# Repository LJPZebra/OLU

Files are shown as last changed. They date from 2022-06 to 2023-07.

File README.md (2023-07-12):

# A Versatile and Open Source One- and Two-Photon Light-Sheet Microscope Design

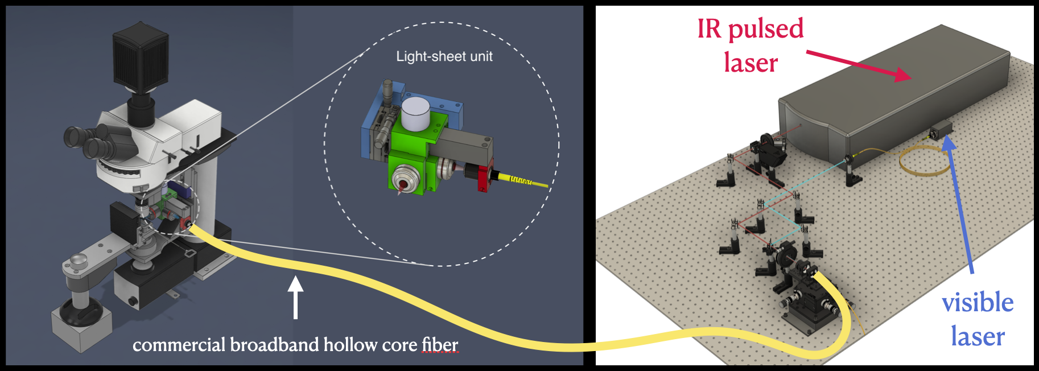
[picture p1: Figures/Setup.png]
Setup


Two-photon light sheet microscopy offers great potential for a range of biological applications, but its practical implementation is impeded by the high cost of laser sources, the complexity of construction, and the challenges associated with adapting to existing microscope setups. Here, we release an open-source design that addresses these limitations by providing detailed building instructions for the transformation of a brightfield microscope into a versatile one- and two-photon light sheet system.
Our design incorporates a specially designed broadband hollow core fiber, enabling the simultaneous utilization of an expansive pulsed laser source from another setup alongside a visible laser. This integration allows for uncompromised image resolution and speed. Furthermore, the design reduces the complexity of construction, alignment, and overall cost, thereby significantly enhancing the accessibility of this technology.

## BUILDING INSTRUCTIONS:

Here we provide a comprehensive online tutorial that features step-by-step building instructions along with 3D animations, illustrations of the construction process, detailed information on the underlying physical principles, and rationale for components selection. In conjunction with the availability of commercially accessible and connectorized broadband optical fiber, our aim is to promote greater accessibility and affordability in the field of multiphoton light-sheet microscopy. To access this online resource, please follow the links provided below: 

1. [Build first a multicolor one-photon version of the microscope](1P_Multicolor_System.md) with fiber delivery of lasers in the visible spectrum with a standard single-mode optical fiber technology.

2. [Upgrade the one-photon unit into a two-photon system](2P-Upgrade.md) by exploiting advanced hollow core fiber technology.

## Citation:

If you use the hardware designs, please cite us:

[A Versatile and Open Source One- and Two-Photon Light-Sheet Microscope Design](https://biorxiv.org/cgi/content/short/2023.07.10.548107v1)

Thomas Panier\*, Geoffrey Migault\*, Antoine Hubert, Hugo Trentesaux, Benoît Beaudou, Georges Debrégeas, Volker Bormuth

https://biorxiv.org/cgi/content/short/2023.07.10.548107v1

https://github.com/LJPZebra/OLU/assets/38736127/4a50b8ec-c064-456c-bfb1-02f57ff8efe5

<!--- 
## Explorable 3D model of the full system

[<img width="600" alt="FullSystem_3D-Model" src="Figures/FullSystem_3D-Model.png">](https://a360.co/41PexBK)

[<img width="600" alt="2P_laser_injection_3D-Model" src="Figures/2P_laser_injection_3D-Model.png">](https://a360.co/3JVrDGn)

Click the images to open the model browser.

## 3D Animation of the functionality of the system

https://github.com/vbormuth/OLU/assets/38736127/af95fe67-40c8-4dab-be80-82982df7b801

## Slow scan mode

https://user-images.githubusercontent.com/113037893/207926697-6573f5d4-6586-4915-aaef-1366d4b2105a.mp4

## Fast scan mode

https://user-images.githubusercontent.com/113037893/207927665-f9e60bf5-719b-4414-81f9-21bd3844fda7.mp4

## High-resolution zebrafish brain scans (elav3:H2B-GCaMP6)

* Left: one-photon mode excited @ 488nm
* Right:  two-photon mode excited @ 915nm

https://user-images.githubusercontent.com/38736127/178161973-748767bf-004d-487c-9377-4582a705d8d7.mp4

## Spontaneous brain activity recorded in a two-photon mode

https://user-images.githubusercontent.com/38736127/174909302-b3901000-2807-471f-93b6-27f24e98cbe1.mp4

## CAD models

[CAD models](CAD_models)

--->

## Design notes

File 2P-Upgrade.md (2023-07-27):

# Two-photon upgrade

This comprehensive guide provides detailed instructions for upgrading the system to the two-photon configuration. Assuming that you have already built the one-photon version of the system, the upgrade primarily involves two main steps. First, you need to fiber couple a two-photon femtosecond pulsed laser into a negative hollow-core optical fiber. Additionally, the fiber's numerical aperture at the output side should be increased for compatibility with the light-sheet unit. Secondly, if not already implemented, the objectives used in the light-sheet unit must be replaced with objectives optimized for near-infrared transmission. Finally, a filter must be installed in the detection path to block the infrared laser. These modifications will enable efficient two-photon imaging with the system.

# Table of Content

- [Part List](#part-liste)
  * [Custom Parts to Send for Milling](#custom-parts-to-send-for-milling)
- [Building Instructions](#building-instructions)
  * [Multiphoton Light-Sheet Unit](#multiphoton-light-sheet-unit)
  * [A Comprehensive Guide for Achieving Efficient Fiber Coupling of the Femtosecond Two-Photon Laser](#a-comprehensive-guide-for-achieving-efficient-fiber-coupling-of-the-femtosecond-two-photon-laser)
    + [Introducing Our Developed Negative Curvature Hollow Core Crystal Fiber](#introducing-our-developed-negative-curvature-hollow-core-crystal-fiber)
    + [The Optical Path for Laser-to-Fiber Coupling](#the-optical-path-for-laser-to-fiber-coupling)
    + [Tips and Techniques for Laser Coupling into the Broadband Hollowcore Crystal Fiber](#tips-and-techniques-for-laser-coupling-into-the-broadband-hollowcore-crystal-fiber)
    + [Mastering the Handling of Hollow Core Fibers: Tips and Techniques](#mastering-the-handling-of-hollow-core-fibers--tips-and-techniques)
    + [Selecting the Optimal Coupling Lens: Criteria and Considerations](#selecting-the-optimal-coupling-lens--criteria-and-considerations)
    + [Let's Get Started: Building the System](#let-s-get-started--building-the-system)
      - [Coupling the IR Laser into the Broadband Fiber](#coupling-the-ir-laser-into-the-broadband-fiber)
      - [Coupling the Visible Laser into the Broadband Fiber](#coupling-the-visible-laser-into-the-broadband-fiber)
  * [Increasing the Fiber Numerical Aperture for Compatibility with the Light-Sheet Unit](#increasing-the-fiber-numerical-aperture-for-compatibility-with-the-light-sheet-unit)
  * [Modifying the Fluorescence Detection Path to Block Infrared Illumination](#modifying-the-fluorescence-detection-path-to-block-infrared-illumination)
  * [Alignement of the setup](#alignement-of-the-setup)
  * [Example of High-Resolution Zebrafish Brain Recordings in One- and Two-Photon Mode (elav3:H2B-GCaMP6)](#example-of-high-resolution-zebrafish-brain-recordings-in-one--and-two-photon-mode--elav3-h2b-gcamp6-)

<small><i><a href='http://ecotrust-canada.github.io/markdown-toc/'>Table of contents generated with markdown-toc</a></i></small>

# Part List

[List of parts](Partlist.md)

## Custom Parts to Send for Milling
    
These parts are  milled from an aluminum block. If you do not have a mechanical workshop in-house then you can send the *.step files that we provide below to an [online milling service](https://xometry.eu/fr/usinage-cnc-fraisage-cnc/). For parts with threaded holes, join the mechanical drawings to the .step file.
* Custom part for compatibility with a MaiTai laser: [View the 3D model](CAD_models/NanoMax_Pedestal.stl) or [download the CAD model as a step file](CAD_models/NanoMax_Pedestal.step) and the [Mechanical drawing](CAD_models/NanoMax_Pedestal.pdf).

# Building Instructions

## Multiphoton Light-Sheet Unit

The multiphoton light-sheet unit is basically identical in its design to the one-photon multicolor design. To build the two-photon system follow [the building instruction of the 1P-Multicolor system](1P_Multicolor_System.md) but take into account the following modification: 

For both the collimation and illumination objectives (step (9) of the building instruction of the Light-sheet Unit), use the [Olympus LMPLN5xIR/0.1](https://www.olympus-lifescience.com/modules/pdfgen/pdfmaker/en_pdf-export_objectives.7efd53eb1e8b4d509bc1bbe2184a7e28/LMPLN5XIR.pdf?rev=1615725199) objective optimized for near-infrared transmission. Although it is not optimized for visible wavelength, one can use this objective for one-photon imaging as well. To screw it into the light-sheet cube use a [thread adaptor](https://punchout.webdev02.thorlabs.com/thorproduct.cfm?partnumber=RMSA3).

## A Comprehensive Guide for Achieving Efficient Fiber Coupling of the Femtosecond Two-Photon Laser

<!--- ### Historical Background

[IS THIS SECTION useful ?]

Efficient, dispersion-free, and broadband fiber coupling of a two-photon laser source is a long-standing challenge in the field of two-photon microscopy ([Helmchen et al., 2011](http://cshprotocols.cshlp.org/content/2013/10/pdb.top078147.long)) and of fiber optics design ([Wang et al., 2013](https://www.cambridge.org/core/journals/high-power-laser-science-and-engineering/article/hollowcore-photonic-crystal-fibre-for-high-power-laser-beam-delivery/8D2851845D043DA937A93F431D9F9D9C)). The difficulty arises from the fact that standard single-mode optical glass fibers are associated with strong linear and non-linear pulse dispersion, which reduces the two-photon efficiency. Pre-compensation methods are only efficient at low laser powers and are therefore impractical in the context of fast volumetric two-photon imaging, which requires high photonic fluxes. 

The development of single-mode photonic bandgap fibers, in which the light travels through an air-filled hollow core, dramatically reduces dispersion and nonlinear effects and achieves transmission ratios greater than 50% ([Wang et al., 2013](https://www.cambridge.org/core/journals/high-power-laser-science-and-engineering/article/hollowcore-photonic-crystal-fibre-for-high-power-laser-beam-delivery/8D2851845D043DA937A93F431D9F9D9C), [Cregan et al., 1999](https://www.science.org/doi/10.1126/science.285.5433.1537)). These fibers have been successfully used for pulsed laser delivery in the context of multiphoton imaging ([Tai et al., 2004](https://opg.optica.org/abstract.cfm?URI=oe-12-25-6122), [Flusberg et al., 2005](https://opg.optica.org/abstract.cfm?URI=ol-30-17-2272), [Engelbrecht et al., 2008](https://opg.optica.org/abstract.cfm?URI=oe-16-8-5556), [Piyawattanametha et al., 2009](https://opg.optica.org/abstract.cfm?&uri=ol-34-15-2309), [Choi et al., 2014](https://www.nature.com/articles/srep06626)). However, as the light guiding mechanism is based on the creation of an optical bandgap, these fibers only allow single-wavelength transmission and are currently only commercially available for laser wavelengths of 800 nm or 1064 nm (NTK photonics). However, with the rapidly growing collections of genetically encoded actuators and sensors, broadband fiber delivery of the near-infrared spectrum and optimally extended to visible wavelengths, is a prerequisite to taking full advantage of 2P-LSFM in all possible applications while enabling laser source sharing between different setups.

Broadband fiber delivery spanning the visible and the near-infrared spectrum is possible with negative curvature hollow-core photonic crystal fibers (NCF), which do not rely on an optical bandgap to confine the laser light to the fiber's core ([Yu et al., 2016](https://opg.optica.org/abstract.cfm?URI=oe-24-12-12969), [Pryamikov et al., 2011](https://opg.optica.org/abstract.cfm?URI=oe-19-2-1441), [Yu et al., 2012](https://doi.org/10.1364/OE.20.011153)). The simplest cross-sectional geometry of an NCF is based on a ring of touching or non-touching tubes surrounding the core ([Pryamikov et al., 2011](https://opg.optica.org/abstract.cfm?URI=oe-19-2-1441)). Core diameter, tube diameter, inter-tube distance, and tube wall thickness together control the spectral transmission bands, the attenuation level, the quality of higher-order mode suppression, and the sensitivity of the optical properties to bending. Attenuation levels < 0.07 dB/km and bending loss < 0.03 dB/m are reported ([Debord et al., 2017](https://doi.org/10.1364/OPTICA.4.000209)). Due to the minimal lattice structure and the reduced light interaction with the cladding structure, these fibers have very high damage thresholds and can even be used for very high laser energy delivery of up to 100 $\mu\textrm{J}$ peak power when the core is vacuum pumped to reduce nonlinear effects at these high powers ([Li et al., 2019](https://doi.org/10.1016/j.ijleo.2019.163093)). Negative curvature fibers are on the verge of being used in several applications such as laser micromachining and laser surgery. A recent study demonstrated the successful use of a custom HC-NCF with a transmission band of 600 – 830 nm at < 0.3 dB/m attenuation in the design of a handheld two-photon microscopy scanner for human skin autofluorescence ([Sherlock et al., 2016](https://doi.org/10.1002/jbio.201500290)).
--->
### Introducing Our Developed Negative Curvature Hollow Core Crystal Fiber

Together with [GLO Photonics](https://www.glophotonics.fr/), we selected an HC-NCF fiber whose optical characteristics are ideally suited for laser delivery in the context of combined one- and two-photon light-sheet microscopy. 

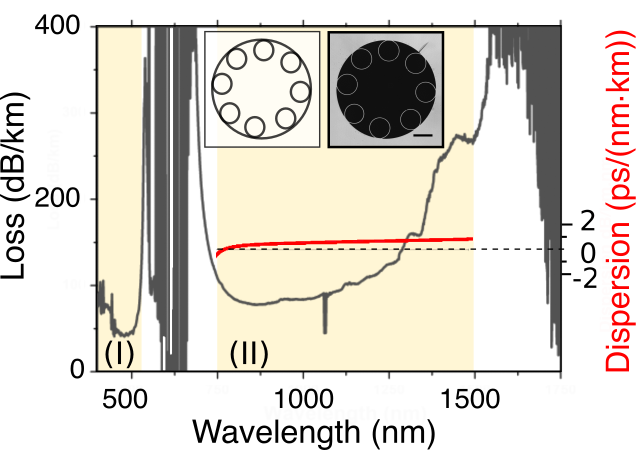
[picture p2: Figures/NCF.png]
NCF
[](Figures/NCF.png)

The outer fiber diameter is 200 ± 2 μm and the fiber coating diameter is 600 ± 30 μm. The fiber has an air-filled 30 μm-in-diameter core surrounded by a ring of eight non-contacting ~10 μm-in-diameter cladding tubes. In this so-called hypocycloid fiber structure, the negative curvature of the core contour is created by the tubes surrounding the core. Tube diameters, inter-tube distance, tube wall thickness, and core size together control the fiber transmission spectrum. They yield two broad transmission bands that are compatible with 1, 2, and 3P imaging, respectively (see figure above): One in the near-infrared from 700 - 1500 nm (I), and another in the visible spectrum from 400 - 535 nm (II). Within these spectral bands, the loss is less than 300 dB/km (corresponding to a transmission efficiency of more than 93% for a one-meter-long fiber), and the pulse dispersion is less than 1 ps/(nm·km) of spectral pulse width. 

The fiber is commercially available as a patch chord cable with standard FC/PC connectors. This proves extremely convenient as it allows one to disconnect and reconnect the fiber to the optical setup without the need for subsequent realignment on either end. The small core diameter compared to the infrared wavelength further ensures near single-mode guidance.

The Gaussian beam properties of the laser are also well preserved at the fiber output with M^2 values of 1.23 and 1.18, measured at 1030 nm and 515 nm laser wavelength respectively. The near-field and far-field profiles are symmetric with minimal ellipticity of 97.25% and 85.57%. The mode field diameters at 1/e^2 are 23 ± 1 μm and 26 ± 1 μm, respectively, which correspond to a fiber's numerical aperture (NA) of approximately 0.02. Due to negligible interactions between the light and the fiber material, the fiber exhibits a very high damage threshold: we could not observe any fiber damage up to the maximal tested peak powers of 40 μJ at 1030 nm and 10 μJ at 515 nm for 400 fs pulses, corresponding to an average laser power of 20W and 4W, respectively. These characteristics demonstrate that high-quality Gaussian beams can be delivered with this fiber across a broad spectral range with high transmission and low dispersion, which is a prerequisite for its application in high-resolution microscopy.

### The Optical Path for Laser-to-Fiber Coupling
The following schematic and [3D model that you can interactively explore](https://a360.co/434IdMt) show a possible optical path for the laser coupling. You can adapt the arrangement to the space availability on your setup (mirror, **M**, lens, **L**, dichroic, **D**, wave plate, **W**, polarizer, **P**, beam trap, **BT**):

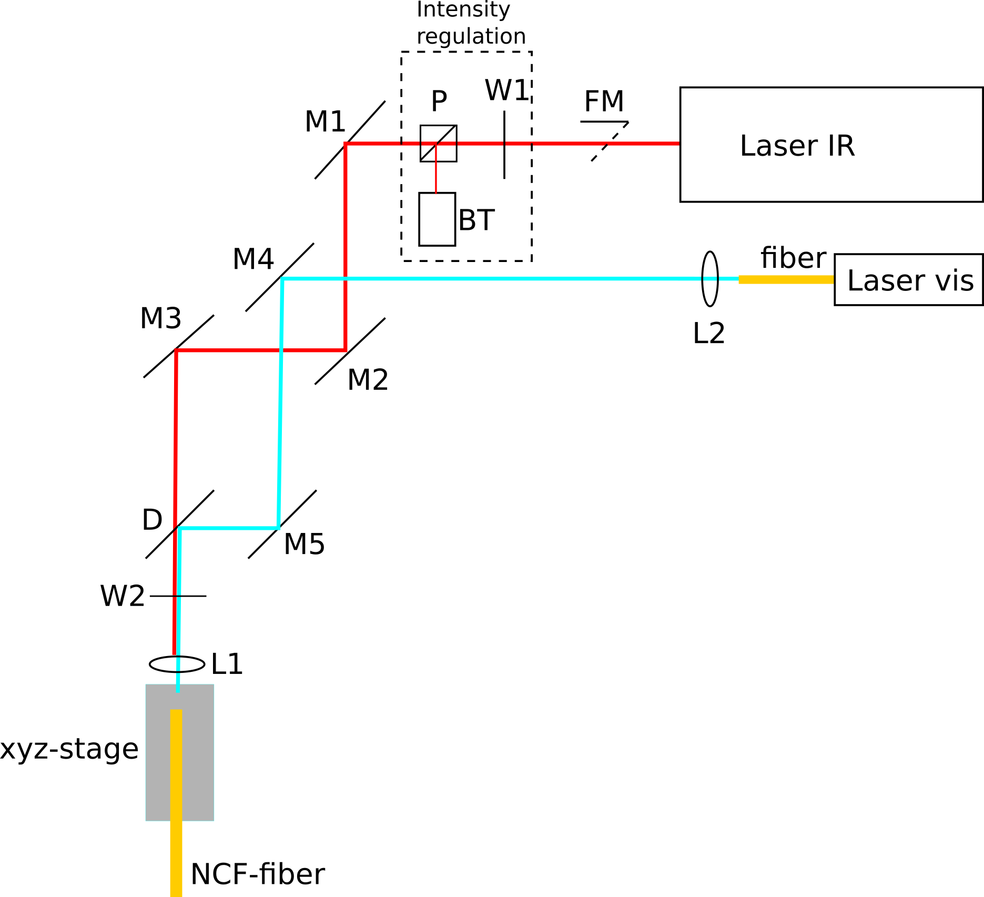
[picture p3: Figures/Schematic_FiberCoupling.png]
Schematic_FiberCoupling
[](Figures/Schematic_FiberCoupling.png)
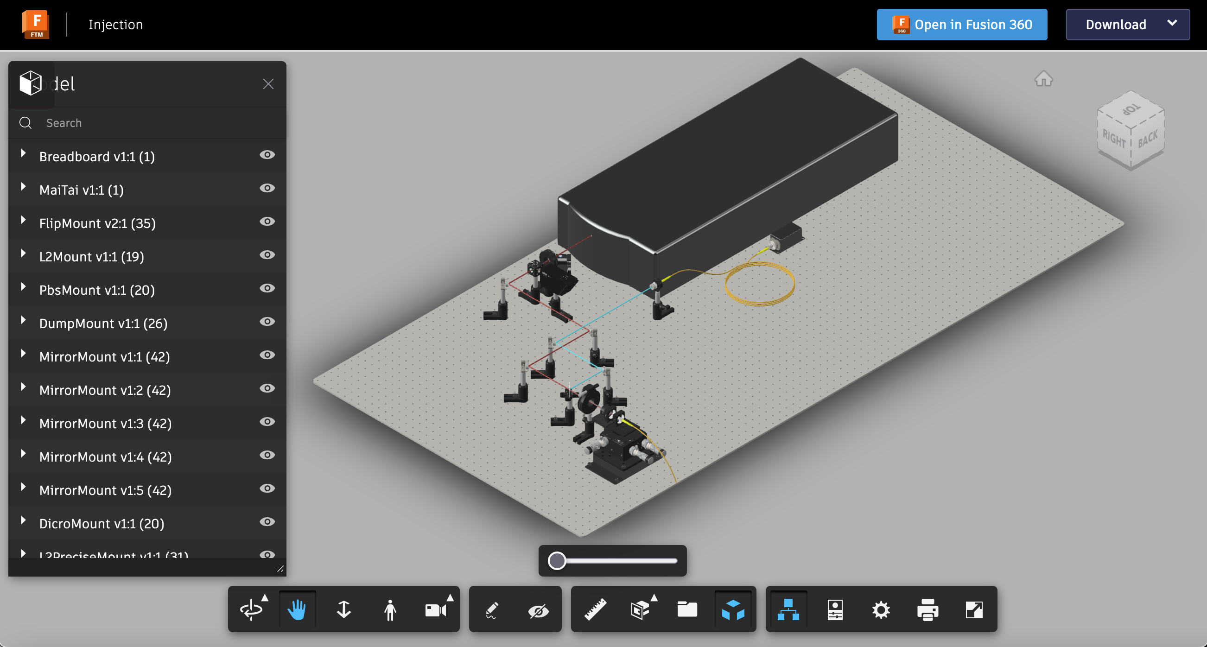
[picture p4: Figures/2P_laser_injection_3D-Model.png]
AlignmentTutorial
[](https://a360.co/3JVrDGn)

If you do not have space on your table you can mount a platform on top of your IR-pulsed laser source and bring the laser beam with a [periscope](https://www.thorlabs.com/newgrouppage9.cfm?objectgroup_id=883) up to the platform. 

In the following, we propose a step-by-step explanation of how to build this optical path and how to align the optical components to achieve optimal fiber coupling. But before we begin, we will give some preparatory notes and general background:

### Tips and Techniques for Laser Coupling into the Broadband Hollowcore Crystal Fiber
For the alignment we will follow a protocol well explained in an excellent YouTube tutorial that you find here and that we advise you to watch carefully before starting. The video explains a first pre-alignment step based on the backpropagation of a laser in the reverse direction. To use this trick first connect a standard single-mode fiber to the coupling unit. Use a fiber tester to inject a visible laser through the fiber. Then follow the steps as in the tutorial to co-align the alignment laser and the IR laser. Then disconnect the fiber and connect the hollow core fiber. If the first step was done correctly you should have enough transmission through the fiber to be able to further optimize the fiber coupling as described in the tutorial. To watch the video just click on the snapshot: 

[AlignmentTutorial](https://www.youtube.com/watch?v=kQvhbJbDG0M)

### Mastering the Handling of Hollow Core Fibers: Tips and Techniques
* Here you find the [fiber spec sheet](https://github.com/vbormuth/OLU/files/9039097/PMC-C-K9005.B2_delivered_2019-01-16.pdf) of our hollow-core negative curvature fiber 
* Attention !: The hollow core fiber front face is not protected and cannot be easily polished, which is a standard procedure used for conventional single-mode fibers. Work clean and remove dust before connecting the fiber to a porte. Also never try to clean the fiber outlet with ethanol or acetone because these solutions will enter the fiber core by capillary forces making the fiber unusable. You can use a [fiber inspection scope](https://www.thorlabs.com/thorproduct.cfm?partnumber=FS201) to inspect the fiber core.

* The fiber has a very high damage threshold but only if the laser is well coupled. So it is advised to do the alignment procedure at low laser power. This improves also laser safety. You can control the laser intensity with a rotatable [lambda wave plate](https://www.newport.com/p/10RP52-2B) installed in series with a [polarizor]([https://www.thorlabs.com/thorproduct.cfm?partnumber=CCM1-PBS25-1064-HP](https://www.thorlabs.com/thorproduct.cfm?partnumber=CCM1-PBS252/M)). 

### Selecting the Optimal Coupling Lens: Criteria and Considerations

* For efficient optical coupling and suppression of higher laser modes, the diameter of the laser spot projected onto the fiber input side has to [match the mode field diameter of the fiber](https://www.thorlabs.com/newgrouppage9.cfm?objectgroup_id=14203). Or in other words, the opening angle of the focused laser beam has to match the numerical aperture of the fiber. Our fiber has a numerical aperture of 0.02 (see [fiber spec sheet](https://github.com/vbormuth/OLU/files/9039097/PMC-C-K9005.B2_delivered_2019-01-16.pdf)). The numerical aperture of the coupling system is given by $\textrm{NA} = \frac{D}{2 f}$, with $D$ the diameter of the laser beam at the position of the coupling lens, and $f$ the coupling lens' focal length.  The laser company normally gives the beam width and the beam divergent angle. In our case, the Ti:Sapphire laser (MaiTai, Coherent, USA) has an output beam waist $<1.2\textrm{mm}$ and a divergent angle of $<0.001\textrm{mrad}$. We measured a beam diameter of 1.6mm at the position where we decided to install the coupling unit and we thus chose a coupling lens with focal length $f = \frac{D}{2\textrm{NA}} = \frac{1.6\textrm{mm}}{2\cdot 0.02} = 40\textrm{mm}$. We got reasonable coupling with the achromatic coupling lens. If you want to further optimize the coupling you can use an [objective](https://www.olympus-lifescience.com/modules/pdfgen/pdfmaker/en_pdf-export_objectives.7efd53eb1e8b4d509bc1bbe2184a7e28/LMPLN5XIR.pdf?rev=1615725199) as coupling lens. And you can install a telescope to adjust the beam diameter to match the fiber numerical aperture with the chosen coupling lens focal distance. Further tips for fiber coupling can be found in the [manual from GLO-photonics](https://github.com/vbormuth/OLU/files/9039094/PIP_PMC-OEM.pdf).
* To measure the laser beam diameter, you may use either a beam profiler (Thorlabs BC207VIS/M) or the [moving knife technique](https://www.researchgate.net/profile/Emerson-Lima-2/publication/23771279_Measurement_of_Gaussian_laser_beam_radius_using_the_knife-edge_technique_Improvement_on_data_analysis/links/00b7d533ec8470fe22000000/Measurement-of-Gaussian-laser-beam-radius-using-the-knife-edge-technique-Improvement-on-data-analysis.pdf?origin=publication_detail). For the latter, fix a razor plate on a [linear translation stage](https://www.thorlabs.com/thorproduct.cfm?partnumber=XRN25C/M). For this use a [thin plate holder](https://www.thorlabs.com/thorproduct.cfm?partnumber=PC2/M), a [right angle clamp](https://www.thorlabs.com/thorproduct.cfm?partnumber=RA90) and a [post system](https://www.thorlabs.com/navigation.cfm?guide_id=52). Then move the knife perpendicular to the laser path step-by-step out of the laser beam while measuring the laser intensity as a function of the knife-edge position. The measured normalized power as a function of knife-edge position,  $x$, can be fitted by  $P_N(x)=0.5\left[1 + erf \left(\frac{x-x0}{w_{e^{-1}}}\right)\right]$. The fit parameter $w_{e^{-1}}$ is the beam radius at $e^{-1}$. You can also read $w_{e^{-1}}$ from the graph as half of the distance between the positions where the normalized power has a value between 0.08 and 0.92. Note that the beam diameter, $D$ ,relevant to calculate the numerical aperture is measured at $e^{-2}$ and is thus given by  $D = 2 \cdot w_{e^{-2}} = 2 \cdot \sqrt{2} w_{e^{-1}}$ <br> <br>

### Let's Get Started: Building the System

#### Coupling the IR Laser into the Broadband Fiber
*	Position the [motorized flip mount](https://www.thorlabs.com/thorproduct.cfm?partnumber=MFF101/M) (**FM**) holding a [protected silver mirror](https://www.thorlabs.com/thorproduct.cfm?partnumber=PF05-03-P01) directly after the infrared laser output to hijack the laser for coupling into the optical fiber. Flipping the mirror allows you to select the setup into which you want to direct the laser. Alternatively, you can use a [beam splitter](https://www.thorlabs.com/newgrouppage9.cfm?objectgroup_id=6208&pn=BS033) to use the laser source on both setups simultaneously. The pertinence of the latter solution depends on the  laser power that you need in both setups for your experiments. For a standard scanning two-photon system, you will generally need less than 100mW. A MaiTai laser has an average output power of 1.8W at 915nm wavelength. With a 90:10% beam splitter and assuming 50% loss of laser power until the sample you can perform light-sheet microscopy with an average laser power of 400mW and two-photon scanning on the standard system with a mean power of 90mW. 
*	Next install the optics to control the laser intensity. Position the [lambda wave plate](https://www.newport.com/p/10RP52-2) and the [polarizor]([https://www.thorlabs.com/thorproduct.cfm?partnumber=CCM1-PBS25-1064-HP](https://www.thorlabs.com/thorproduct.cfm?partnumber=CCM1-PBS252/M)) in series. 
*   Before switching on the laser, prepare for laser safety in the room and wear [laser safety glasses](https://www.thorlabs.com/thorproduct.cfm?partnumber=LG3) to protect your eyes!
*   Install the [power meter](https://www.thorlabs.com/thorproduct.cfm?partnumber=PM130D) to measure the laser power after the polarizer (**P**)
*   Switch on the laser and rotate the wave plate until the transmitted laser power is minimal. 
*   Increase again slowly the laser power until you start seeing the laser spot on the [IR detection card](https://www.thorlabs.com/thorproduct.cfm?partnumber=VRC5)
*   Close the laser shutter
*   Position the two [protected silver mirrors](https://www.thorlabs.com/thorproduct.cfm?partnumber=PF05-03-P01) (**M1, M2 & M3**) mounted in [kinematic mirror mounts](https://www.thorlabs.com/thorproduct.cfm?partnumber=POLARIS-K05#ad-image-0). With mirror **M2** and **M3** you will later align the laser with the fiber axis. A good distance between these two mirrors is about 20cm. Adjust the height of the [posts](https://www.thorlabs.com/thorproduct.cfm?partnumber=TR75/M) that hold the mirrors with the height of your laser beam. Tighten them on the optical table with [Universal Post Holders](https://www.thorlabs.com/thorproduct.cfm?partnumber=UPH50/M#ad-image-0).
*  Install the [long pass dichroic mirror](https://www.thorlabs.com/thorproduct.cfm?partnumber=DMLP650R) (**D**) that is transparent for the infrared laser but reflects the visible spectrum. This will allow later the coupling of an additional visible laser into the same fiber. 
*	Mount the differential **xyz-translation stage** ([MAX313D/M](https://www.thorlabs.com/thorproduct.cfm?partnumber=MAX313D/M#ad-image-0)) at about 20cm from the mirror **M3**. With this stage, you will position the fiber outlet precisely into the focal point of the coupling lens. You might have to mount this stage on a platform to match the beam height  (**Custom piece for compatibility with a MaiTai laser: [Mechanical drawing](CAD_models/NanoMax_Pedestal.pdf), [.stl file](CAD_models/NanoMax_Pedestal.stl) and [.step file](CAD_models/NanoMax_Pedestal.step)**). Alternatively, you can lower the beam path with a [periscope](https://www.thorlabs.com/newgrouppage9.cfm?objectgroup_id=883).  
*  Install the [half-wave plate](https://www.newport.com/p/10RP52-2B) (W2) mounted in a [high-precision rotation mount](https://www.thorlabs.com/thorproduct.cfm?partnumber=PRM1/M) to adjust the polarization of the laser.  For the highest signal in two-photon microscopy, the laser polarisation needs to be aligned with the light-sheet plane. You can do this later by rotating this waveplate until you observe a maximum of the fluorescence signal. 
*  Fix the  [mounting bracket](https://www.thorlabs.com/thorproduct.cfm?partnumber=AMA009) onto the non-moving front of the **xyz-stage** and mount onto it a [SM1-Compatible Flexure Stage Mount](https://www.thorlabs.com/thorproduct.cfm?partnumber=HCS031) to hold the coupling lens **L1**.
*  Screw the coupling lens into the holder ([AC254-040-B-ML](https://www.thorlabs.com/thorproduct.cfm?partnumber=AC254-040-B-ML)) 
*  Mount the [SM1-compatible flexure stage mount](https://www.thorlabs.com/thorproduct.cfm?partnumber=HCS031) onto the moving platform of the xyz-stage and screw into this mount the [FC/PC fiber adapter plate with its external SM1 threading](https://www.thorlabs.com/thorproduct.cfm?partnumber=SM1FC2). This FC/PC adapter will later receive the optical fiber.
*	Attach the [single mode fiber](https://www.thorlabs.com/thorproduct.cfm?partnumber=P1-460B-FC-2) for prealignment to the FC/PC adaptor plate. 
*	Attach the other side of the fiber to the [cable continuity tester](https://www.flukenetworks.com/datacom-cabling/fiber-testing/VisiFault-Visual-Fault-Locator) for pre-alignment.
*	Switch on the red laser of the continuity tester. You should see the laser exiting out of the other side of the fiber
*	Adjust the distance of the coupling lens (**L1**) relative to the fiber outlet until the red laser light from the continuity tester is well collimated by the coupling lens. 
*	Now follow the alignment steps explained in the YouTube tutorial. Eventually, watch the video again.
*	Now that you know how to do it ensure laser safety in the room and wear [laser safety glasses](https://www.thorlabs.com/thorproduct.cfm?partnumber=LG3) to protect your eyes!
*	Prepare a [VIS/IR Detector Card](https://www.thorlabs.com/thorproduct.cfm?partnumber=VRC2) to visualize the invisible infrared laser
*   Open the laser shutter.
*   Now move the two mirrors **M2** and **M3** to co-align the red laser and the IR laser as was explained in the video.
*   Switch off the laser shutter
*   Detach the single-mode fiber from the coupling unit
*   Attach the [negative curvature broadband hollow core fiber](https://github.com/vbormuth/OLU/files/9039097/PMC-C-K9005.B2_delivered_2019-01-16.pdf) to the coupling unit.
*   Position the power meter before the coupling lens and adjust the power to about ???mW.
* Install an FC/PC adaptor plate and fix to it the other end of the fiber. Install the power meter just after the fiber to measure the transmitted laser power.
* Open again the laser shutter. You should measure laser transmission through the fiber.
* Now adjust the mirrors **M2** and **M3** as was described in the video until you get > 90% laser transmission. 
* Close the laser shutter 

#### Coupling the Visible Laser into the Broadband Fiber
* Fix the [fiber coupled laser](https://github.com/vbormuth/OLU/files/9057780/WEBSITE-Datasheet-LBX-488.pdf) onto the table.
* Position mirror **M3** and **M4** with a distance of about 20cm between each other such that mirror **M4** is placed about 20cm from the coupling lens. As mirrors choose again [protected silver mirrors](https://www.thorlabs.com/thorproduct.cfm?partnumber=PF05-03-P01) mounted in [kinematic mirror mounts](https://www.thorlabs.com/thorproduct.cfm?partnumber=POLARIS-K05#ad-image-0) to align the laser with the fiber axis. Select the length of the [posts](https://www.thorlabs.com/newgrouppage9.cfm?objectgroup_ID=9079) compatible with the height of your laser beam.
* Attach the fiber splitter to the laser that you purchased with the prealigned fiber coupler.
* Install a [prealigned fiber collimators](https://www.thorlabs.com/thorproduct.cfm?partnumber=F110FC-532) **L2** that you mount into a [kinematic mirror mount](https://www.thorlabs.com/thorproduct.cfm?partnumber=KM05/M#ad-image-0) using an [adaptor](https://www.thorlabs.com/thorproduct.cfm?partnumber=AD11BA) and positioned onto the adequate [posts](https://www.thorlabs.com/thorproduct.cfm?partnumber=TR1) and its [universal post holder](https://www.thorlabs.com/thorproduct.cfm?partnumber=UPH1).
     * We selected the collimation lens focal distance with the formula: $f_{collimation} = f_{coupling} \cdot  \frac{NA_{fiber}}{NA_{laser fiber}} = 40\textrm{mm} \cdot \frac{0.02}{0.13}$
which boils down to the fact to choose the collimation lens focal distance such that the collimated laser beam diameter matches the diameter of the infrared beam that we previously coupled into the fiber using the chosen coupling lens. 
* Attach one of the outputs of the fiber coupler to this collimator lens. 
* Attach the other side to the FC/PC connector plate on the **xyz-stage** of the coupling unit. If the fiber is to short you can extend it with a [fiber-to-fiber connector](https://www.thorlabs.com/thorproduct.cfm?partnumber=ADAF1) and the single mode fiber that you have used in the previous pre-alignment step.
* prepare laser safety and switch on the laser at the lowest power possible where you can see with the [VIS/IR Detector Card](https://www.thorlabs.com/thorproduct.cfm?partnumber=VRC2) the laser.
* Now use the mirror **M3** and **M4** to co-align the two laser beams that travel in the reverse direction through the system as explained in the alignment YouTube tutorial. 
* Switch off the laser and replace the single-mode fiber that is connected to the coupling unit with the negative curvature fiber.
* Switch the laser again on.
* You should detect with the power meter a transmission through the fiber.
* Adjust mirror **M3** and **M4** until you have more than 75% percent of transmission

At 915nm wavelength, the central two-photon absorption peak of GFP and of its calcium sensitive derivative GCaMP, we delivered through 1.5m fiber length 100fs laser pulses with 98% power transmission efficiency and minute pulse dispersion of 28nm (1dB/km·nm) that we fully precompensated with the Deepsee element of the MaiTai laser source. At 488nm,  the one-photon excitation maximum of GFP and GCaMP, we achieved a transmission efficiency of ~75%. 

[Go back to the main page](README.md)

## Increasing the Fiber Numerical Aperture for Compatibility with the Light-Sheet Unit

* The collimation and illumination objective form a one-to-one telescope. If we would simply connect the hollow core fiber to the light-sheet unit as we did in the 1P-Multicolor system then the light-sheet thickness would correspond to the mean field diameter of the hollow core fiber which is $23\mu m$ ([fiber spec sheet](https://github.com/vbormuth/OLU/files/9039097/PMC-C-K9005.B2_delivered_2019-01-16.pdf)). To get the same resolution as in the one-photon implementation we have to install an extra lens after the fiber to demagnify the laser waist from the fiber output to about $5\mu m$ and at the same time to increase the divergence angle of the laser to match the numerical aperture of the collimation objective. The numerical aperture of the fiber is 0.02 and thus a factor 5 times smaller compared to the numerical aperture of the detection objective.
* With a [lens](https://www.thorlabs.com/thorproduct.cfm?partnumber=C151TMD-B) with a focal distance of f = 2mm and a numerical aperture of 0.5 you can demagnify the laser output from the fiber by a magnification of m = 0.2. Mount this lens via an [adaptor](https://www.thorlabs.com/thorproduct.cfm?partnumber=S05TM06) into the [lens tube](https://www.thorlabs.com/thorproduct.cfm?partnumber=SM05M10) which you prepared in step (5-7) of the [manual of the 1P-Multicolor unit](1P_Multicolor_System.md).  
* Place the lens at a distance $s = f \left( \frac{1}{m} - 1\right) = f \left( 5 - 1\right) = 4 \cdot f = 8\textrm{mm}$ after the fiber output. The lens refocuses the laser at a new position $s' = f \cdot \left[ 1 + \frac{1}{s/f - 1} \right] = 1.2 \cdot f = 2.4\textrm{mm}$ after the lens down to a waist of $w_0^{'} = m \cdot w_0 = 0.2 \cdot 23 \mu m = 4.6\mu m$ with an angle of divergence of the laser corresponding to a numerical aperture of $m \cdot 0.02 = 0.1$ thus matching the numerical aperture of the collimation objective.

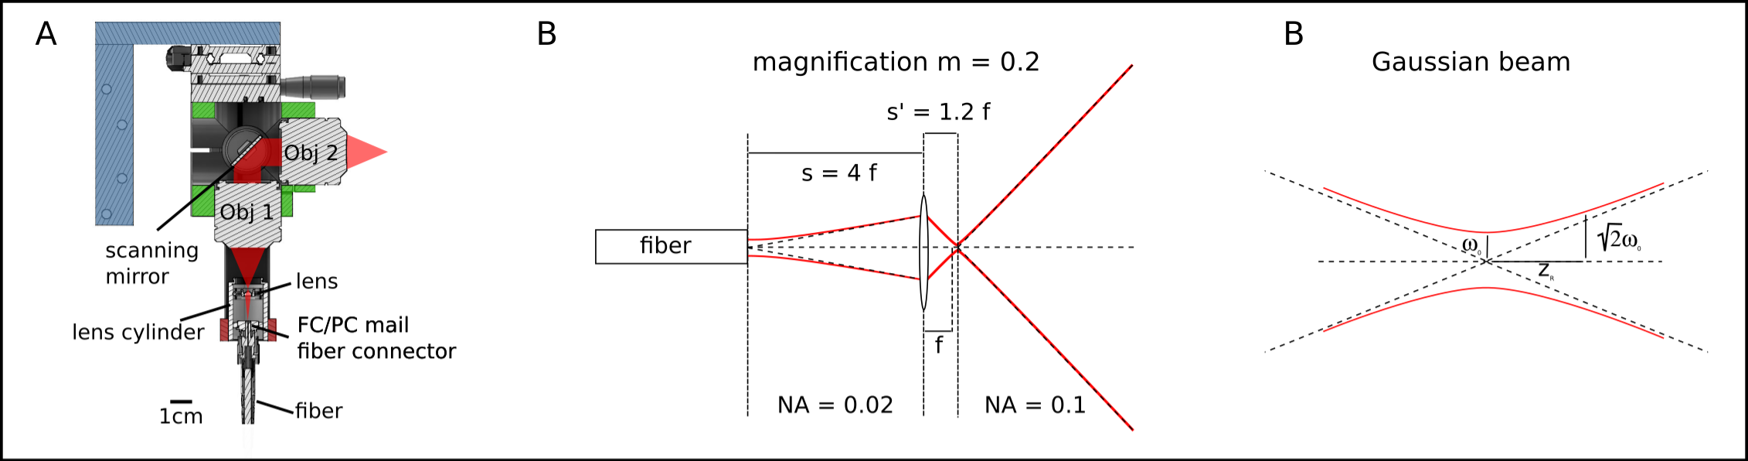
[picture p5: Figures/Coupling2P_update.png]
NA_Expander


[Focusing of spherical Gaussian beams by Sidney A. Self](https://citeseerx.ist.psu.edu/viewdoc/download?doi=10.1.1.1091.571&rep=rep1&type=pdf)

## Modifying the Fluorescence Detection Path to Block Infrared Illumination
* Install in addition the [multiphoton short-pass emission filter](https://www.semrock.com/filterdetails.aspx?id=ff01-750/sp-25) to block also the pulsed infrared laser source.

## Alignment of the setup

* Align the system in one-photon mode following the instructions provided for the [1P-Multiphoton system](1P_Multicolor_System.md). This alignment procedure will also align the two-photon pathway.

* Align the polarization of the two-photon laser within the light-sheet plane. Visualize the two-photon laser using a fluorescein solution. Rotate wave plate W2, which is installed in front of the xyz-translation stage in the fiber coupling optical pathway. Continue rotating the wave plate until the fluorescence signal is maximized, indicating the optimal position.

* Note that the alignment and transmission efficiency of the hollow-core fiber in the infrared are not affected by fiber bendings. However, bending the fiber will indeed affect the polarization by changing its direction and ellipticity. Once you have set the rotation angle of wave plate W2, it is crucial not to move the fiber any further. If the fiber is inadvertently moved, the rotation angle of the wave plate will need to be readjusted accordingly to ensure optimal performance. For further information regarding the dependency of light-sheet fluorescence microscopy on polarization, please refer to [Vito et al. Optic Express 2020](https://opg.optica.org/boe/fulltext.cfm?uri=boe-11-8-4651&id=433823).

## Example of High-Resolution Zebrafish Brain Recordings in One- and Two-Photon Mode (elav3:H2B-GCaMP6)

* Left: one-photon mode excited @ 488nm
* Right:  two-photon mode excited @ 915nm

https://github.com/LJPZebra/OLU/assets/38736127/a6df432b-a5b5-4ccf-8948-ba9a2f0df49e

## Go back:
[README](README.md)

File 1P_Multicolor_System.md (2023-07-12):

# The Multicolor One-Photon Light Sheet Design

This comprehensive guide provides detailed instructions for building the one-photon light-sheet system. Whether your ultimate goal is to construct the two-photon system or utilize the one-photon configuration, we highly recommend starting with the installation of the one-photon system. This sequential approach allows you to gain a solid foundation and a better understanding of the system's components and functionality, which will facilitate a smoother transition to the advanced two-photon configuration if desired.

The construction of the system can be done on two levels. At the first level, the light-sheet unit is a standalone light source. This basic configuration allows you to perform light-sheet imaging experiments in the same manner as you would normally acquire epifluorescence images or stacks. At the second level, the concerted motion of the light-sheet and imaging objective is computer-controled and allows you to perform fast, high-precision volumetric scans. This advanced level of control opens up additional capabilities and enhances the versatility of the light-sheet unit for various imaging applications.

If your ultimate goal is to set up the two-photon version, you have the option to directly use optics optimized for infrared transmission in the initial one-photon installation. This strategic choice ensures compatibility and paves the way for a seamless transition to the two-photon configuration at minimal cost by avoiding the need for component replacements when upgrading to the two-photon version.

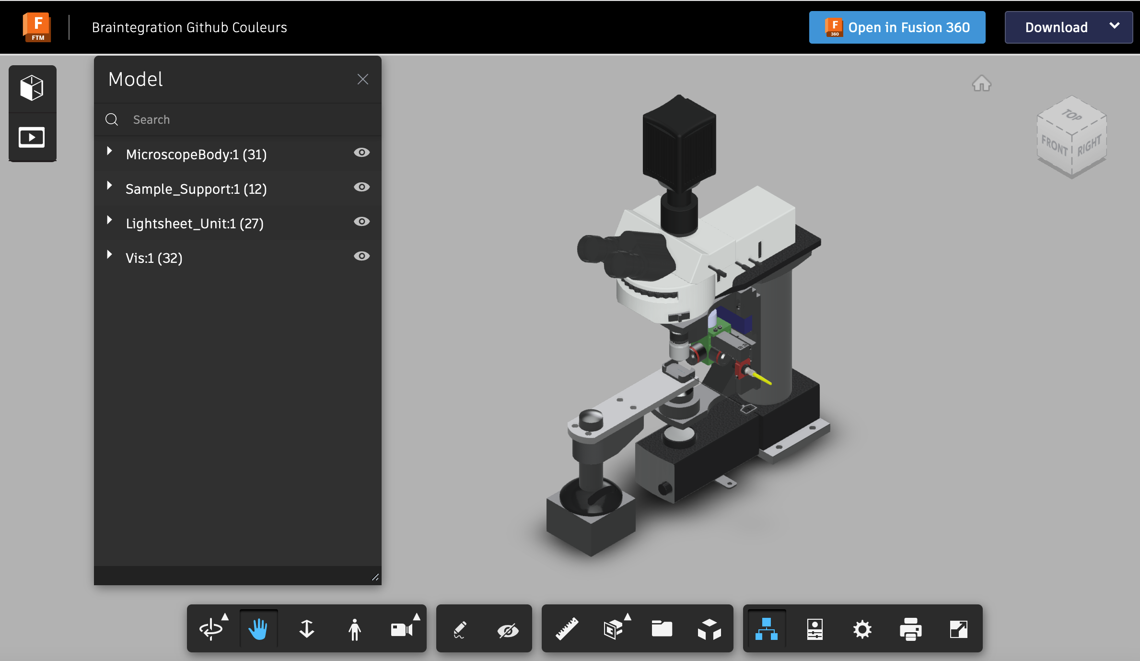
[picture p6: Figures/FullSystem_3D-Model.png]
FullSystem_3D-Model
[](https://a360.co/41PexBK)

Click the images to open the model browser.

# Table of Content

- [Building Instructions](#building-instructions)
  * [Purchase List](#purchase-list)
  * [Custom Parts](#custom-parts)
    + [Pieces to Send for Milling](#pieces-to-send-for-milling)
    + [Pieces for 3D Printing](#pieces-for-3d-printing)
  * [Screw kit](#screw-kit)
  * [Let's Start to Assemble](#let-s-start-to-assemble)
    + [The Light-Sheet Unit](#the-light-sheet-unit)
      - [Laser and Fiber Coupling](#laser-and-fiber-coupling)
      - [Adapt the Scientifica Scope to receive the light-sheet unit](#adapt-the-scientifica-scope-to-receive-the-light-sheet-unit)
      - [Assemble the light-sheet unit](#assemble-the-light-sheet-unit)
      - [Laser Alignement](#laser-alignement)
    + [The Detection Path](#the-detection-path)
    + [Driving the Light-Sheet Unit](#driving-the-light-sheet-unit)
      - [Mode 1: Stand-Alone Light-Sheet Source Without the Need for Additional Computer Interfacing](#mode-1--stand-alone-light-sheet-source-without-the-need-for-additional-computer-interfacing)
      - [Mode 2: A Computer Controlled Light-Sheet Scanner](#mode-2--a-computer-controlled-light-sheet-scanner)
    + [The Sample Chamber Holder and Sample Chamber](#the-sample-chamber-holder-and-sample-chamber)
    + [Ensuring Laser Safety](#ensuring-laser-safety)
    + [Now Let's Align the System](#now-let-s-align-the-system)
  * [Photos of the System in Combination with an Electrophysiology System:](#photos-of-the-system-in-combination-with-an-electrophysiolgy-system-)
  * [Example Recordings:](#example-recordings-)
  * [A Conference Talk Presenting the System:](#a-conference-talk-presenting-the-system-)
  * [Upgrade the One-Photon Unit into a Two-Photon System by using a Hollowcore Crystal Fiber](#upgrade-the-one-photon-unit-into-a-two-photon-system-by-using-a-hollowcore-crystal-fiber)

<small><i><a href='http://ecotrust-canada.github.io/markdown-toc/'>Table of contents generated with markdown-toc</a></i></small>

# Building Instructions

## Purchase List

[List of parts](Partlist.md)

## Custom Parts

### Parts to Send for Milling
    
These parts are  milled from an aluminum block. If you do not have a mechanical workshop in-house then you can send the *.step files that we provide below to an [online milling service](https://xometry.eu/fr/usinage-cnc-fraisage-cnc/). For parts with threaded holes, join the mechanical drawings to the .step file.
* The light-sheet unit central cube: [View the 3D model](CAD_models/Cube.stl) or [download the CAD model as a step file](CAD_models/Cube.step) and [mechanical drawings](CAD_models/CubeMechanicalDrawings.pdf).
* The fiber holder  : [View the 3D model](CAD_models/FiberHolder.stl) or [download the CAD model as a step file](CAD_models/FiberHolder.step) and [mechanical drawings](CAD_models/FiberHolderMechanicalDrawings.pdf).
* Adaptor plate 1 : [View the 3D model](CAD_models/AdaptorPlate1.stl) or  [download the CAD model as a step file](CAD_models/AdaptorPlate1.step) and [mechanical drawings](CAD_models/AdaptorPlate1MechanicalDrawings.pdf).
* Adaptor plate 2 : [View the 3D model](CAD_models/AdaptorPlate2.stl) or  [download the CAD model as a step file](CAD_models/AdaptorPlate2.step) and [mechanical drawings](CAD_models/AdaptorPlate2MechanicalDrawings.pdf).
* Custom bracket : [View the 3D model](CAD_models/CustomBracket.stl) or  [download the CAD model as a step file](CAD_models/CustomBracket.step) and [mechanical drawings](CAD_models/CustomBracketMechanicalDrawings.pdf).
* Sample chamber holder : [View the 3D model](CAD_models/SampleChamberHolder.stl) or [download the CAD model as step file](CAD_models/SampleChamberHolder.step) and [mechanical drawings](CAD_models/SampleChamberHolderMechanicalDrawings.pdf).
* T-bracket to hold the beam trap : [View the 3D model](CAD_models/TBracket.stl) or [download the CAD model as step file](CAD_models/TBracket.step) and [mechanical drawings](CAD_models/TBracketMechanicalDrawings.pdf).
* Piezoactuator dummy : [View the 3D model](CAD_models/PiezoDummy.stl) or [download the CAD model as step file](CAD_models/PiezoDummy.step) and [mechanical drawings](CAD_models/PiezoDummyMechanicalDrawings.pdf). This piece is only necessary if you do not want to install the piezo actuator required for the fast scan mode.

### Parts for 3D Printing
* [Sample chamber](CAD_models/SampleChamber.stl). You can download the [CAD model as step file](CAD_models/SampleChamber.step) to send it to your 3D printing service.

## Screw kit
You will need Hex Head Socket Cap metric screws:

| type          | length (cm)   | amount |
| ------------- | ------------- | ------ |
| M3            | 10            | 4      |
| M4            | 30            | 4      |
| M4            | 25            | 2      |
| M4            | 20            | 5      |
| M4            | 10            | 2      |
| M5            | 30            | 2      |
| M6            | 20            | 3      |

E.g. this [Srew kit](https://www.amazon.fr/huruirui-hexagonales-int%C3%A9rieures-inoxydable-rangement/dp/B0BNC63J21/ref=sr_1_21?__mk_fr_FR=%C3%85M%C3%85%C5%BD%C3%95%C3%91&crid=3MCQH28G0NEHV&keywords=vis%2BM3%2BM4%2BM5%2BM6%2B10%2F20%2F25%2F30&qid=1684324658&s=industrial&sprefix=vis%2Bm3%2Bm4%2Bm5%2Bm6%2B10%2F20%2F25%2F30%2Cindustrial%2C58&sr=1-21&th=1) will do it. 

## Let's Start to Assemble

### The Light-Sheet Unit

#### Laser and Fiber Coupling

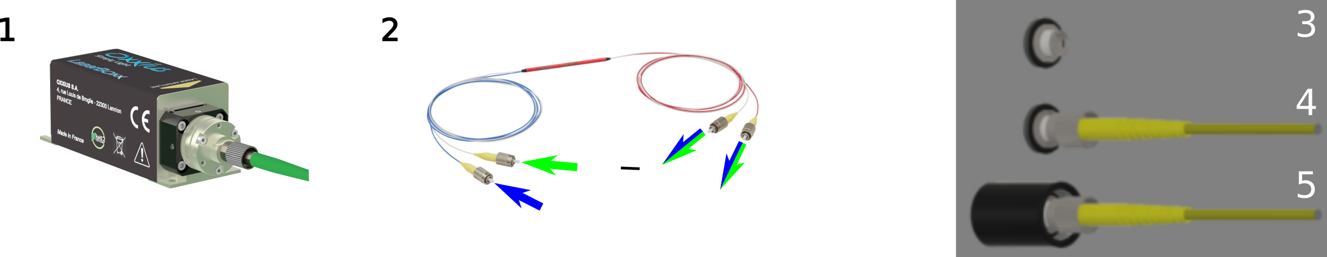
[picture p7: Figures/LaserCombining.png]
[](Figures/LaserCombining.png)

(1) Purchase [continous lasers](https://www.oxxius.com/category-products/continuous-and-modulated-lasers/) whose wavelength are adapted to your favorite fluorescence probes.  We use a blue 488nm and a green 561nm laser. Choose the option with [prealigned fiber coupler](https://github.com/vbormuth/OLU/files/9057780/WEBSITE-Datasheet-LBX-488.pdf).

(2) To combine the two lasers into a single-mode fiber, attach the two inputs of the [fiber optic coupler](https://www.thorlabs.com/thorproduct.cfm?partnumber=TW470R5F2) to the FC/PC connector of each laser. The blue and green lasers will be combined and available at both output fiber ports.

(3-5) Assemble the Fiber support tube: Take the [FC/PC connector](https://www.thorlabs.com/thorproduct.cfm?partnumber=SM05FC#ad-image-0) which will later hold the optical fiber that delivers the laser. Screw the connector into the [lens tube](https://www.thorlabs.com/thorproduct.cfm?partnumber=SM05M10) (black) but not too far so that you can easily attach and detach the optical fiber. Fix the connector with the two retaining rings.

#### Adapt the Scientifica Scope to receive the light-sheet unit

You will need to unscrew the bracket that holds the objective support plate from the original Scientifica setup.

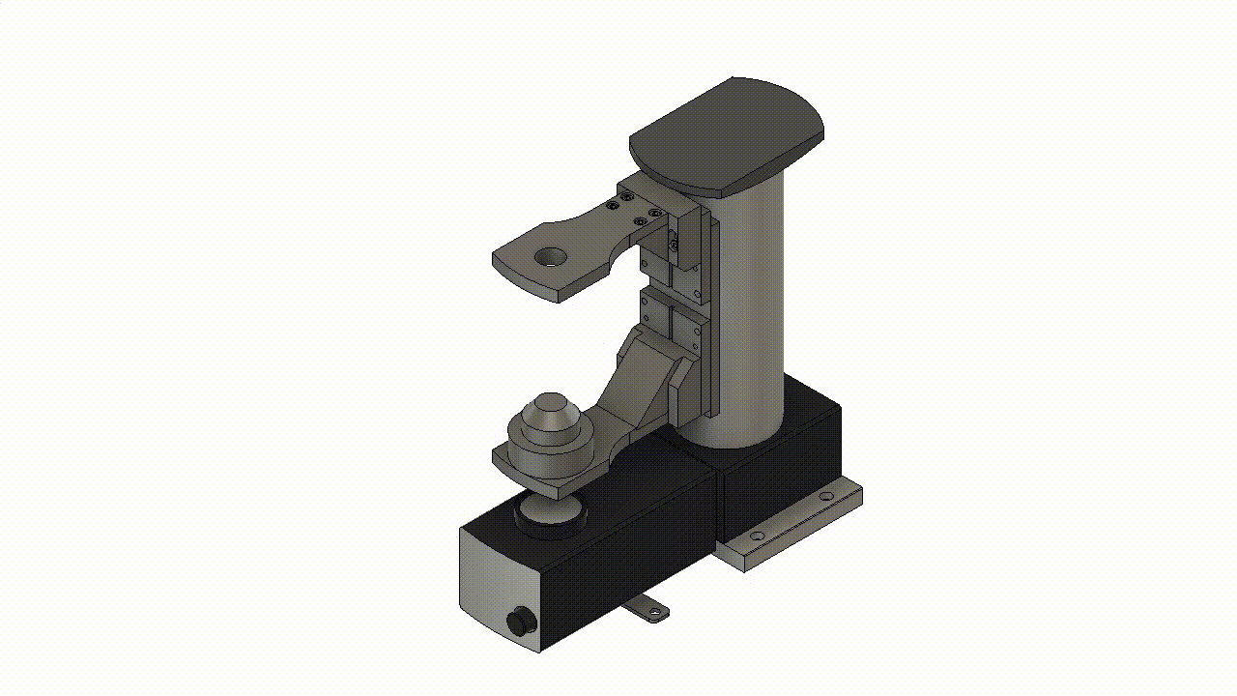
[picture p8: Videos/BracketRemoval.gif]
[](/Videos/BracketRemoval.gif)

This bracket will then be replaced with a custom bracket that has holes to allow the light sheet unit to be attached to the Scientifica system in the next steps. 

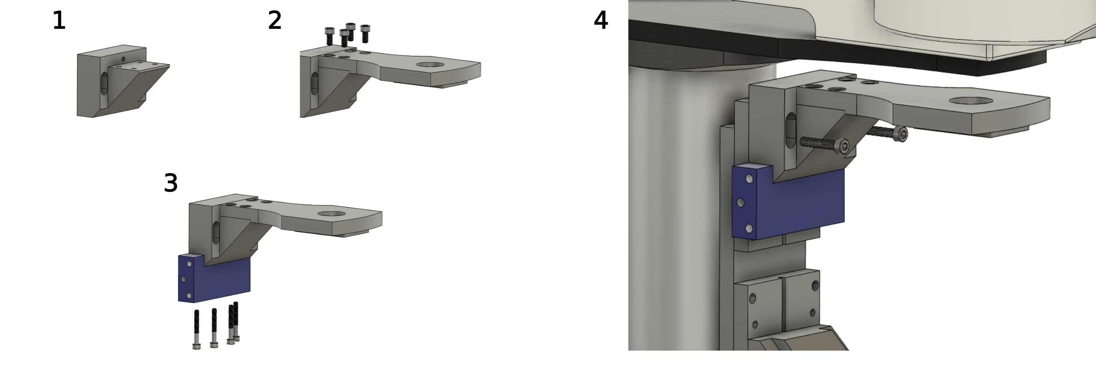
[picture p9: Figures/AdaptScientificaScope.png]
[](Figures/AdaptScientificaScope.png)

(1-2) Attach the top plate (previously unscrewed from the Scientifica Scope) to the [Custom Bracket](CAD_models/CustomBracket.stl) (custom piece) using the original screws.

(3) Attach the [Adapter Plate 1](CAD_models/AdaptorPlate1.stl) (custom part) with four M4x30 screws.

(4) Attach the assembly to the topmost Z-stage of the microscope with two original screws.

#### Assemble the light-sheet unit

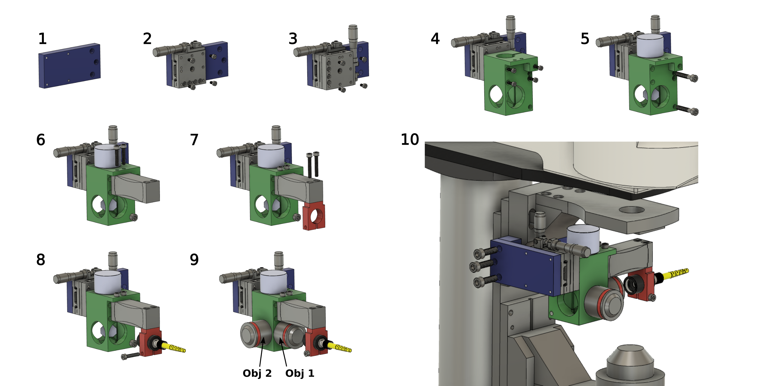
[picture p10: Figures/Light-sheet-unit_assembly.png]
[](Figures/Light-sheet-unit_assembly.png)

(1) Start from the [Adapter Plate 2](CAD_models/AdaptorPlate2.stl) (blue, custom piece).

(2) Attach the Horizontal Manual Stage to the Adapter Plate 2 with the four M3 screws included with the stage.

(3) Attach the Vertical Manual Stage to the Horizontal Manual Stage with the four M3 screws included with the stage.

(4) Attach the [Light-Sheet Unit Central Cube](CAD_models/Cube.stl) (green, custom piece) to the Vertical Manual stage with four M3x10 screws.

(5) Insert the [Galvanometer Mirror](https://www.thorlabs.com/thorproduct.cfm?partnumber=GVS011) (light blue), align it at 45° relative to the sides of the Light-sheet Cube, and fasten it in place with two M5x30 screws.

(6) Attach the [Piezocrystal (PZ 400 SG OEM)](https://www.piezosystem.com/product/pz-400-oem/). If you want to start with a simple low-cost version that uses only the slow scanning mode then install instead the [Piezo Dummy](CAD_models/PiezoDummy.stl) (custom piece) to the Light-sheet Cube with two M4x20 screws.

(7) Attach the [Fiber Holder](CAD_models/FiberHolder.stl) (red, custom piece) to the Piezo with two M4x25 screws.

(8) Insert the Fiber support tube (see points 3-5) into the Fiber Holder, fasten it with one M4x20 screw and attach one of the output fibers of the fiber optic coupler to the connector (2).

(9) Screw in the [Zeiss Plan-Neofluar Objectives (5x/0.16 M27)](https://www.micro-shop.zeiss.com/en/us/shop/objectives/420330-9901-000/Objective-EC-Plan-Neofluar-5x-0.16-M27). If your ultimate goal is to build the two-photon version then you should use instead the  [Olympus LMPLN5xIR/0.1](https://www.olympus-lifescience.com/modules/pdfgen/pdfmaker/en_pdf-export_objectives.7efd53eb1e8b4d509bc1bbe2184a7e28/LMPLN5XIR.pdf?rev=1615725199) objectives, which is optimized for near-infrared transmission.

(10) Attach the Light-sheet Unit to the Scientifica Scope by fixing the adapter Plate 2 onto the Adapter Plate 1 using three M6x20 screws.

#### Laser Alignement

Before turning on the laser, prepare the room for laser safety (remove any jewelry, make sure no one is in the path of the laser, and that the laser does not hit any reflective surfaces). Unscrew the focusing objective (Obj 2) of the light-sheet unit. Switch on the galvanometric mirror and then switch on the laser at low power. By moving the fiber support tube (black) relative to the fiber holder (red), adjust the distance of the fiber outlet to the collimation objective (Obj 1) until the beam exiting the cube is well collimated.  

Next, carefully center the beam in the opening where Obj 2 will be located by adjusting the orientation of the galvanometer mirror. Once this is done, secure the mirror position with the fixing screw. Secure Obj 2 in place again by screwing it in. 

### The Detection Path

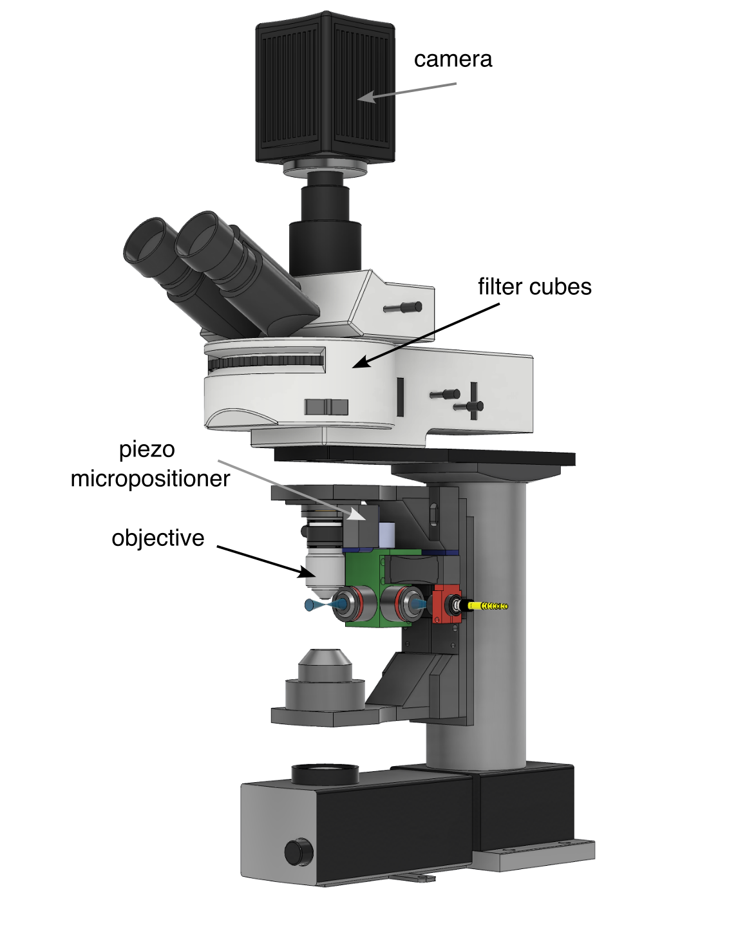
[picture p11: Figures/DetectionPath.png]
DetectionPath
[](Figures/DetectionPath.png)

To configure the detection path, use the standard ports and configuration of the Scientifica scope.

* Use a detection objective that is best adapted to your application. If you want to install the fast z-scan mode then attach the objective via an [objective scanning piezo system](https://www.pifrance.fr/fr/produits/platines-de-nanopositionnement-a-structure-deformable/support-objectif-pifoc-et-scanners-pinano-pour-la-microscopie/p-725-pifoc-objective-scanner-with-long-travel-range-200375/). 
<!--- We use an [Olympus 20x objective](https://www.thorlabs.com/catalogpages/Obsolete/2019/N60XW-PF.pdf) in combination with a [tube lens](https://www.thorlabs.com/thorproduct.cfm?partnumber=AC254-150-A) of 150mm in focal length yielding a 16x magnification. --->
* Position the filters into the filter wheel adapted to your application. For GFP imaging:
     * a [notch filter to block the 488nm laser line](https://www.thorlabs.com/thorproduct.cfm?partnumber=NF488-15)
     * a [GFP Emission Filter](https://www.thorlabs.com/thorproduct.cfm?partnumber=MF525-39).
* Attach the camera to the camera port. In our systel, we use the [Hamamatsu ORCA-Flash4.0 V3 camera](https://www.hamamatsu.com/content/dam/hamamatsu-photonics/sites/documents/99_SALES_LIBRARY/sys/SCAS0134E_C13440-20CU_tec.pdf)

### Driving the Light-Sheet Unit

The light-sheet unit can be operated in two modes:

#### Mode 1: Stand-Alone Light-Sheet Source Without the Need for Additional Computer Interfacing

To drive the galvanometer, a simple and affordable [function generator](https://www.amazon.com/Generator-Precision-Dual-Channel-Arbitrary-Frequency/dp/B07H8CF2WV/ref=sr_1_3?crid=BMHYRYNELBAO&keywords=function+generator+JDS6600&qid=1685005539&sprefix=function+generator+jds6600%2Caps%2C273&sr=8-3) is sufficient. Set the mirror to oscillate at approximately 400Hz with a triangular or sawtooth waveform.

If your image acquisition software allows the acquisition of z-stacks by controlling either the motorized stage of the z-focus or the piezo objective scanner, then you can operate the light-sheet unit in two modes.

**Slow Scan Mode:**

Even if you have not installed the piezo-control of the objective and optical fiber, you can still perform volumetric recordings. Simply control the movement of the objective using the motorized stage of the Scientifica scope, similar to a standard epifluorescence recording. Since the light-sheet unit is attached to the same stage as the objective, it will move along with the objective, ensuring that the light-sheet always illuminates the focal plane.

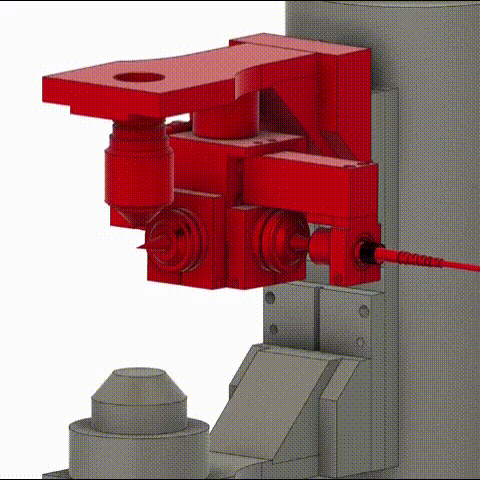
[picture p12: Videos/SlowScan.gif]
[](/Videos/SlowScan.gif)

#### Mode 2: A Computer-Controlled Light-Sheet Scanner

**Fast Scan Mode:**

If you have installed a piezoactuator for both the imaging objective and the fiber, you can achieve high precision and fast volumetric recordings. Synchronizing the movement of the fiber with that of the objective is crucial to ensure that the light sheet remains in the focal plane of the objective throughout the volumetric acquisition.

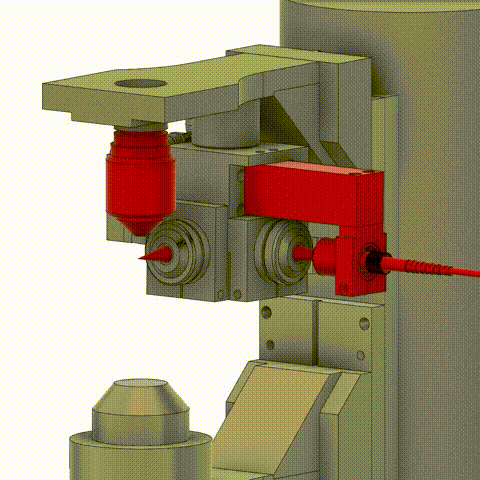
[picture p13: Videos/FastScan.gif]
[](/Videos/FastScan.gif)

<!--- To achieve this synchronization, utilize your microscope control software to drive the objective scanner, and control the piezocrystal responsible for moving the fiber using the monitor signal from the controller of the focus scanner.
Calibrate the voltage with a [potentiometer???LINK??????](add link here ??????) --->

* To control the light-sheet volumetric scanning you can use our [custom developed control software](https://github.com/LaboJeanPerrin/Lightsheet) written in Matlab. Via a national instrument card [PCIe-6363](https://www.ni.com/fr-fr/support/model.pcie-6363.html), this software simultaneously drives the objective piezo scanner, the galvomirror and the piezo that moves the fiber in order to scan the light-sheet through the sample. The software is open source. 

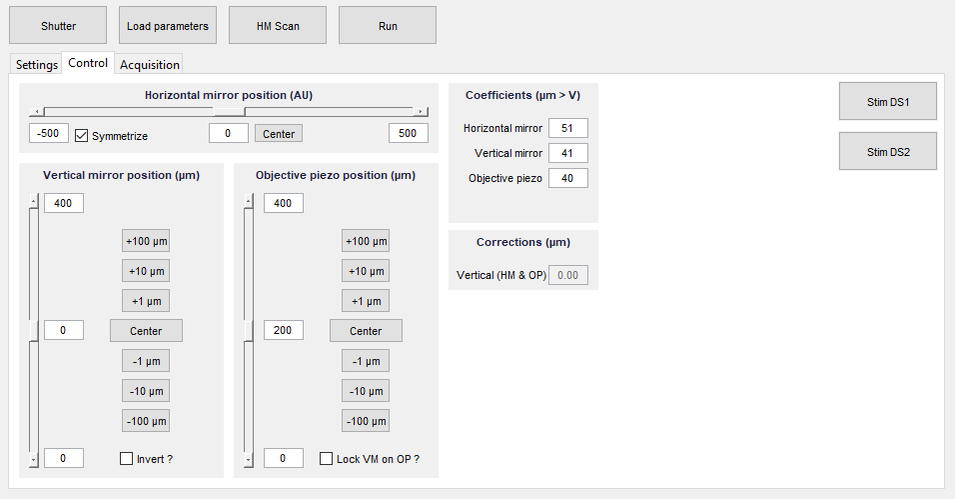
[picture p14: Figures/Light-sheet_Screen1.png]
Light-sheet_Screen1
[](Figures/Light-sheet_Screen1.png)
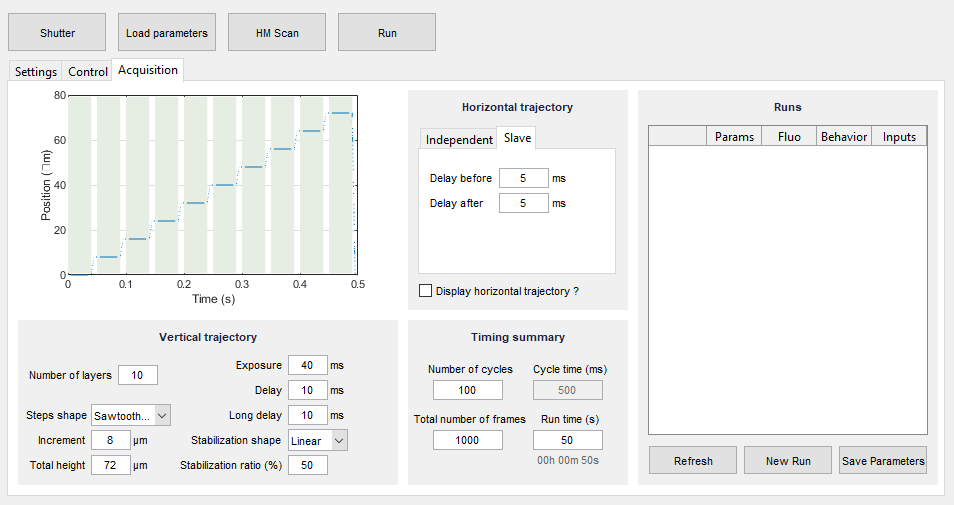
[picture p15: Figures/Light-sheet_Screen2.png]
Light-sheet_Screen2
[](Figures/Light-sheet_Screen2.png)

* Alternatively, you can use:
    *  [ScanImage](https://www.scientifica.uk.com/products/vidrio-technologies-scanimage), the control software provided by Scientifica   
    *  [Micromanager](https://micro-manager.org/), which supports the control of all Scientifica stages as well as of most common objective scanners from e.g. Physical Instrument or Piezo Jena.
    *  or the open-source python software presented here: https://www.frontiersin.org/articles/10.3389/fcell.2022.875044/full

### The Sample Chamber Holder and Sample Chamber

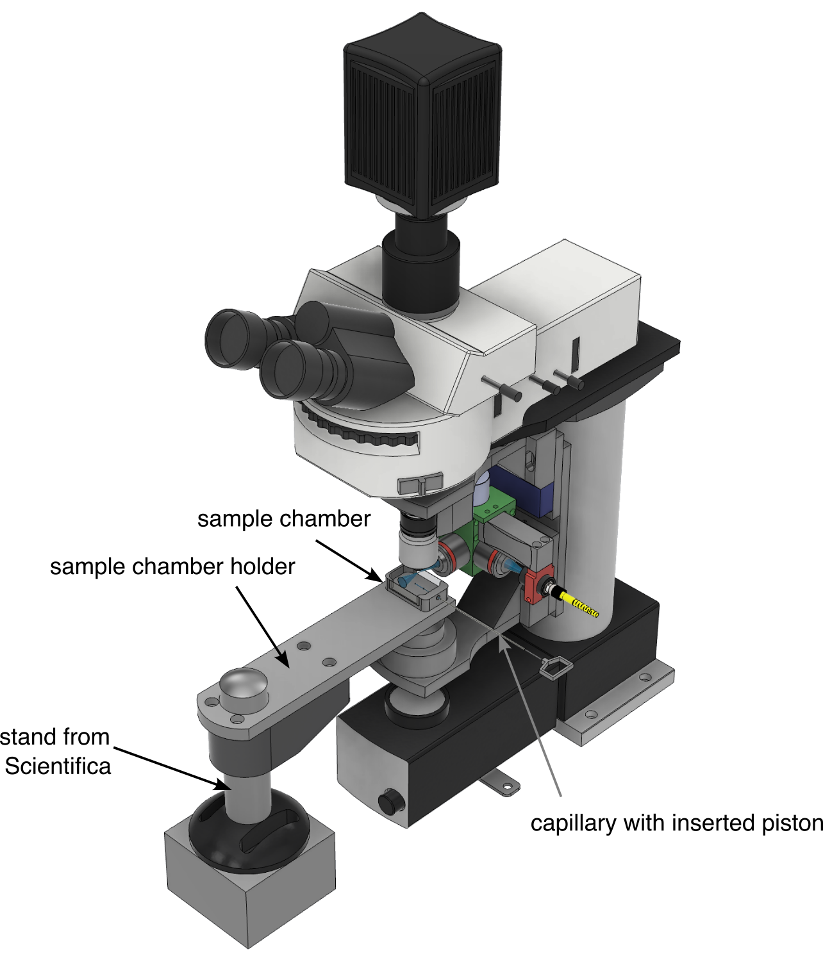
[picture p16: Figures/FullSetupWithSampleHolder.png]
SampleHolder
[](Figures/FullSetupWithSampleHolder.png)

* Install the [sample chamber holder](CAD_models/SampleChamberHolder.stl) (custom part). 
* 3D print the [sample chamber](CAD_models/SampleChamber.stl). 

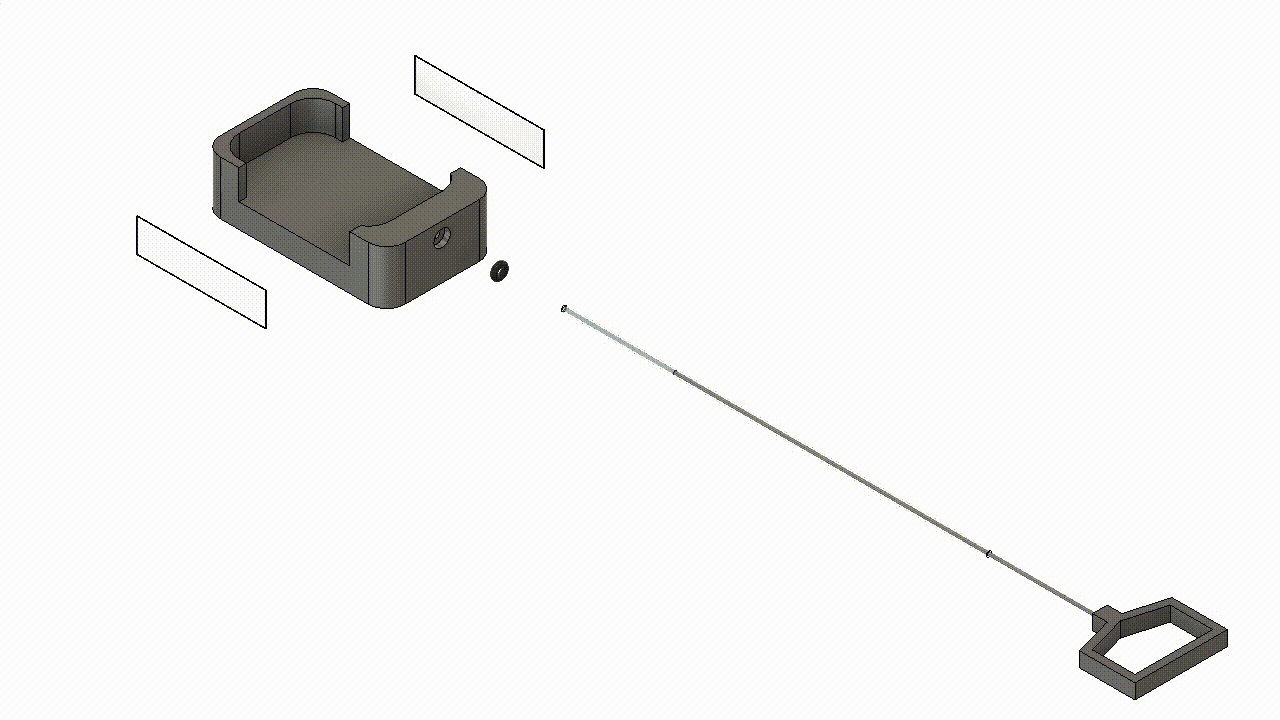
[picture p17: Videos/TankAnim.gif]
[](/Videos/TankAnim.gif)

*  Take the 3D printed [sample chamber](CAD_models/SampleChamber.stl) and use [cyanoacrylate](https://uk.rs-online.com/web/p/glues/0473455) or [UV-curing adhesive](https://www.thorlabs.com/thorproduct.cfm?partnumber=NOA68) to glue a glass window on each side as well as an [O-ring](https://www.oring.fr/joint-torique/22-1.html?search_query=&results=45) into the hole on the short side, which will allow you later to introduce and position the sample via a [capillary](https://www.alphalabs.co.uk/5-000-2050) (inner diameter 0.85mm, outer diameter 1.47mm, length 115mm) for the imaging sessions. 

*  Place the sample chamber into the predefined opening of the sample chamber holder.

[](https://user-images.githubusercontent.com/38736127/178137631-2c89b6cf-9c1a-4c7f-b7f9-2d27c1fac82d.png)

<!--- https://www.fishersci.fi/shop/products/plunger-acura-capillary-micropipettes/p-8481034 --->

### Ensuring Laser Safety

Protect the experimenter from the laser by installing a [beam blocker](https://www.thorlabs.com/thorproduct.cfm?partnumber=LB2) in front of the sample chamber. Fix the [T-bracket](CAD_models/TBracket.stl) (custom piece) with two M4x20 screws to the [sample chamber holder](CAD_models/SampleChamberHolder.stl) and then fix the beam blocker with two M4x10 screws to the T-bracket. 
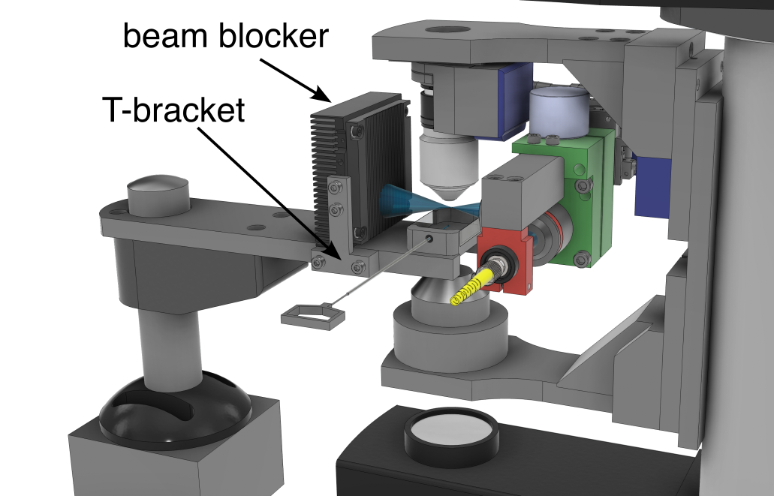
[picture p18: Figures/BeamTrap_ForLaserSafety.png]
BeamTrap_ForLaserSafety
[](Figures/BeamTrap_ForLaserSafety.png)

### Now Let's Align the System
* Fill the sample chamber with water and add a few drops of a 1.5mM fluorescein solution into the water-filled sample chamber to visualize the laser. Switch on the laser at low power until you can see the fluorescence laser profile. Be careful not to look directly into the laser and to keep working at low power (<1mW after the second illumination  objective) for alignment. 
* The use of fluorescein requires cleaning with ethanol or isopropanol after alignment to remove residual fluorophores that may cause imaging noise. 
* It is also possible to use an agarose cylinder and to observe the scattered light from the laser, to do this remove the filter between the detection objective and the camera and follow the same procedure.
* Align the laser waist under the detection objective by moving the entire light-sheet forming unit with the x-translation stage
* Switch on the camera and align the laser into the focal plane of the detection objective by moving the light-sheet forming unit with the z-translation stage until you see a sharp image of the laser beam with the camera. If you do not see the laser beam,  move the galvanometer mirror to bring it within the field of view.

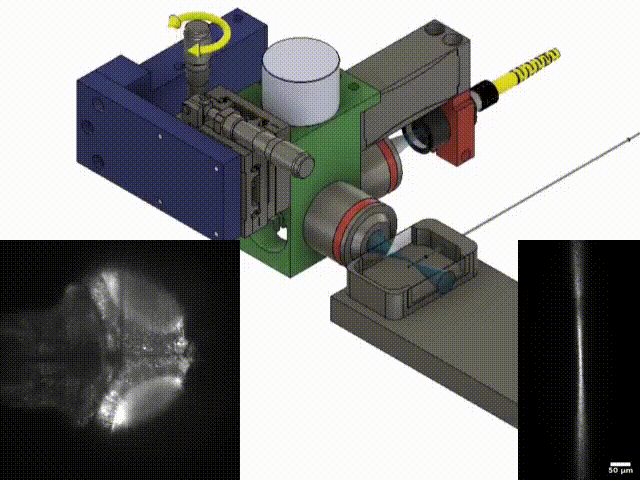
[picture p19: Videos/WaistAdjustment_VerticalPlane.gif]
[](/Videos/WaistAdjustment_VerticalPlane.gif)

* Precisely align the laser waist in the center of the field of view using the x-translation stage

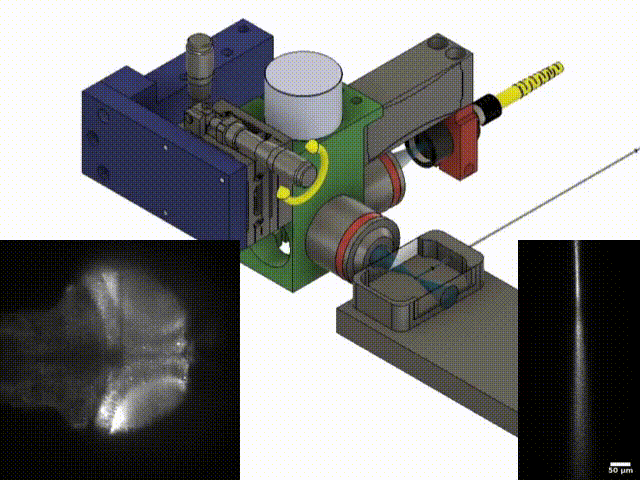
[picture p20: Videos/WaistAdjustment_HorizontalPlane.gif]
[](/Videos/WaistAdjustment_HorizontalPlane.gif)

* Remove the fluorescein solution from the sample chamber and clean it. 
* Now generate the light sheet by driving the galvanometer with a saw tooth pattern either with a function generator or via the control software (see above). Adjust the amplitude of the movement such that the light sheet covers the field of view.
* Now you can place your preferred sample into the light sheet and image it. Fine-tune the z-position and x-position of the light-sheet until you get the sharpest image possible.

* you can now produce 3D scans of your sample by manually moving the objective focus of the microscope or by recording 3D time-lapse movies using your microscope control software. 
* Troubleshooting:
    if your image is not uniformly sharp throughout the field of view, the light sheet might be tilted with respect to the focal plane of the detection objective.  In this case, you can correct this by tilting slightly the entire unit. For this, untighten the screws that connect the unit via the adapter plate to the microscope translation stage. Use a sheet of paper as a spacer between the adapter plate and the stage to tilt the unit in the correct direction once the screws are tighten. Repeat this procedure until your image is in focus across the entire field of view.

## Pictures of the System in Combination with an Electrophysiology System:

BraintegrationSetup

ZoomOnLightsheetUnit

## Example Recordings:

Using the green laser. Shown is a high-resolution recording of a zebrafish brain (6dpf) with a pan-neuronally expressed red calcium indicator (elav3-jRGECO):

https://github.com/LJPZebra/OLU/assets/38736127/308ce3c6-fe21-4a75-a082-1cd4b1d38281

## A Conference Talk Presenting the System:

[AlignmentTutorial](https://www.youtube.com/watch?v=7h87vXg7FHM)

## Upgrade the One-Photon Unit into a Two-Photon System by using a Hollowcore Crystal Fiber

[Click here for detailed instructions](2P-Upgrade.md)

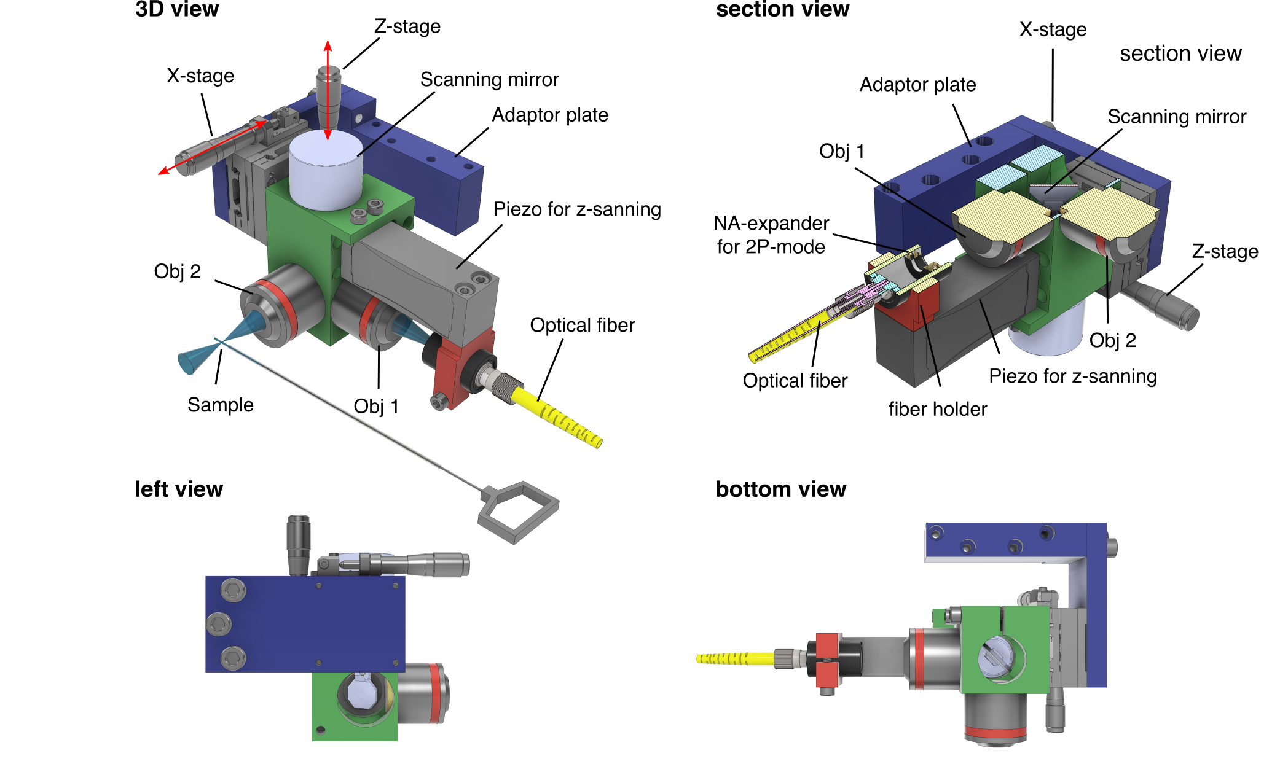
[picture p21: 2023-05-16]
Figures/LU_different_views.png

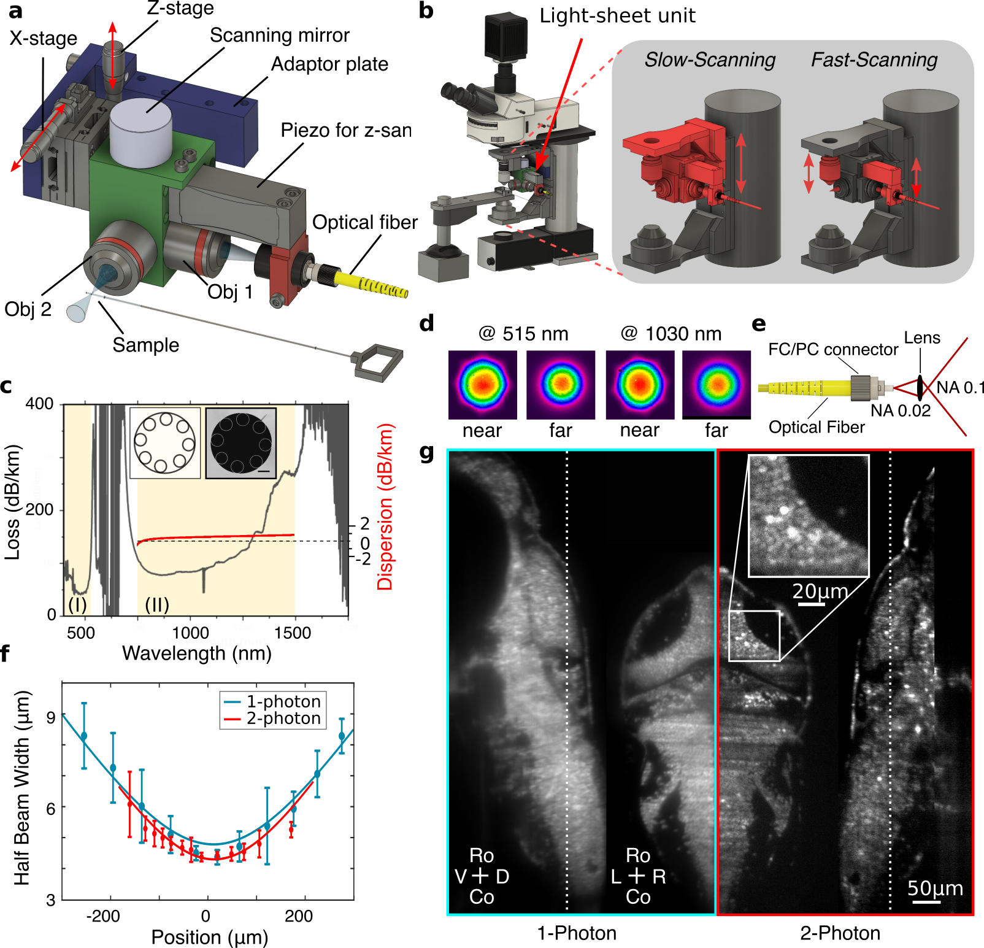
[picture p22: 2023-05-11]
Figures/CompilationFigure.png

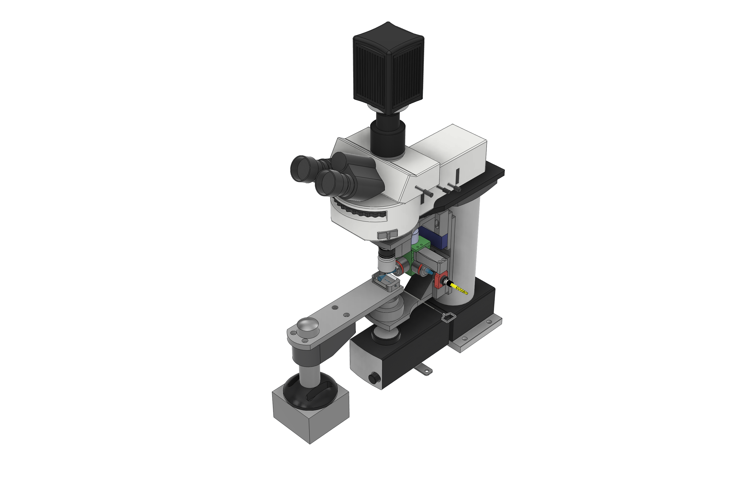
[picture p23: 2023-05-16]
Figures/FullSystem.png

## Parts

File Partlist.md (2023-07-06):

# One-Photon Multicolor System: Parts List

|                     |                                              |                      |                                     | **Slow Scan** | **Fast Scan** |
|---------------------|----------------------------------------------|----------------------|-------------------------------------|-----------|------------------|
|                     | **PART**                                     | **SOURCE**           | **REFERENCE**                       | **Amount**| **Amount**       |
| **Laser & Fiber**   | Continuous laser at 488 nm with fiber coupler| Oxxius               | LBX-488-50-CSB-PP                   | 1         | 1         |
|                     | Optical fiber (single mode)                  | Thorlabs             | P1-460-FC-2                         | 1         | 1         |
|                     | Lens tube                                    | Thorlabs             | SM05M10                             | 1         | 1         |
|                     | **Optional**: Second Continuous laser at other wavelength  | Oxxius     |                                     | 1         | 1         |
|                     | **Optional**: 50:50 Fiber Optic Couplers                   | Thorlabs   | TW470R5F2                           | 1         | 1         |
| **Light-Sheet Unit** | Collimation & illumination objectives       | Zeiss                | EC Plan-Neofluar 5x/0.16 M27 (FWD=18.5mm) | 2     | 2         |
|                     | Lens tube                                    | Thorlabs             | SM05M10                             | 1         | 1         |
|                     | FC/PC Fiber Adapter Plate with External SM05 | Thorlabs             | SM05FC                              | 1         | 1         |
|                     | z-piezo nanopositioner + Amplificator        | Piezo Jena           | "PZ 400 OEM SG + E-440-111          |           | 1         |
|                     | Galvanometer mirror                          | Thorlabs             | GVS011                              | 1         | 1         |
|                     | Power supply for Galvo mirro                 | Thorlabs             | GPS011-EC                           | 1         | 1         |
|                     | Function generator                           | Agilent              | EDU33211A                           | 1         | 1         |
|                     | Acquisition board                            | National Instruments | NI PCIe-6363                        |           | 1         |
| **Microscope**      | Microscope body                              | Scientifica          | Scientifica SliceScope Pro 6000     | 1         | 1         |
| **Detection Path**  | Detection objective (NA 0.95, 25x)           | Leica                | HC FLUOTAR W VISIR                  | 1         | 1         |
|                     | Objective piezo drive +  Driver              | Piezo Jena           | Mipos 500 SG,Triptics + NV 40/1 CLE | 1         | 1         |
|                     | GFP filter (525 nm)                          | Thorlabs             | MF525-39                            | 1         | 1         |
|                     | Notch filter (488 nm)                        | Thorlabs             | NF488-15                            | 1         | 1         |
|                     | Camera (sCMOS)                               | Hamamatsu            | C13440 V3                           | 1         | 1         |
| **Sample Chamber**  | Capillary + pistons                          | alphalabs            | 5-000-2050                          | 1         | 1         |
|                     | O-rings                                      | www.oring.fr         | 101300                              | 1         | 1         |
|                     | Beam Block                                   | Thorlabs             | LB2                                 | 1         | 1         |

# Two-Photon Upgrade: Parts List

|                         | PART                                                          | SOURCE          | REFERENCE                    | Amount |
|-------------------------|---------------------------------------------------------------|-----------------|------------------------------|--------|
| **Laser & Fiber**       | Femtosecond tunable laser                                     | Spectra-Physics | MaiTai 90077043              | 1      |
|                         | Precompensator                                                | Spectra-Physics | Deep See                     | 1      |
|                         | Negative curvature fiber                                      | Glophotonics    | PMC-C-9005 B2                | 1      |
| **Laser-to-Fiber Coupling** | Motorized Filter Flip Mount with Ø1" Optic Holder, M4 Tap | Thorlabs        | MFF101/M                     | 1      |
|                         | High-Precision Rotation Mount                                 | Thorlabs        | PRM1/M                       | 2      |
|                         | Half-Wave Plate                                               | Newport         | 10RP52-2B                    | 2      |
|                         | Polarizing Beamsplitter Cube                                  | Thorlabs        | CCM5-PBS202/M                | 1      |
|                         | Beam Trap                                                     | Thorlabs        | BT610/M                      | 1      |
|                         | Protected Silver Mirrors                                      | Thorlabs        | PF05-03-P01 - Ø1/2"          | 5      |
|                         | Mirror Mount                                                  | Thorlabs        | POLARIS-K05 - Polaris® Ø1/2" | 5      |
|                         | Hex Key Adjusters  (4 per pack)                               | Thorlabs        | HKTS-5/64                    | 1      |
|                         | Optical Post                                                  | Thorlabs        | TR75/M                       | 5      |
|                         | Universal Post Holder                                         | Thorlabs        | UPH50/M                      | 5      |
|                         | 3-Axis NanoMax Stage, Differential Drives                     | Thorlabs        | MAX313D/M                    | 1      |
|                         | Long, Fixed Mounting Bracket, 56 mm Long                      | Thorlabs        | AMA009                       | 1      |
|                         | FC/PC Fiber Adapter Plate with External SM1                   | Thorlabs        | SM1FC2                       | 1      |
|                         | SM1-Compatible Flexure Stage Mount                            | Thorlabs        | HCS031                       | 1      |
|                         | Injection lens (40 mm)                                        | Thorlabs        | AC254-040-B-ML               | 1      |
|                         | fiber-to-fiber connector (Ceramic)                            | Thorlabs        | ADAF1                        | 1      |
| **NA-Expander**         | NA expander lens (f = 2.00 mm, NA = 0.50, ARC: 600 - 1050 nm) | Thorlabs        | C151TMD-B                    | 1      |
|                         | Adapters for M6 x 0.5 Threaded Aspheres                       | Thorlabs        | S05TM06                      | 1      |
| **Accessories**         | IR Detector Card, 700 - 1400 nm                               | Thorlabs        | VRC5                         | 1      |
|                         | Power meter                                                   | Thorlabs        | PM130D                       | 1      |
|                         | Fiber Inspection Scope                                        | Thorlabs        | FS201                        | 1      |
|                         | Cable Continuity Tester                                       | Fluke Networks  | VisiFault                    | 1      |
|                         | Laser safety glasses                                          | Thorlabs        | LG3                          | 1      |
| **Light-Sheet Unit**    | Collimation & Illumination objective (NA 0.1, 5x)             | Olympus         | LMPLN5xIR/0.10               | 2      |
|                         | RMS to M27 Adapter                                            | Thorlabs        | RMSA3                        | 1      |
| **Detection Path**      | Multiphoton short-pass emission filter                        | Semrock         | FF01-750/SP-25               | 1      |

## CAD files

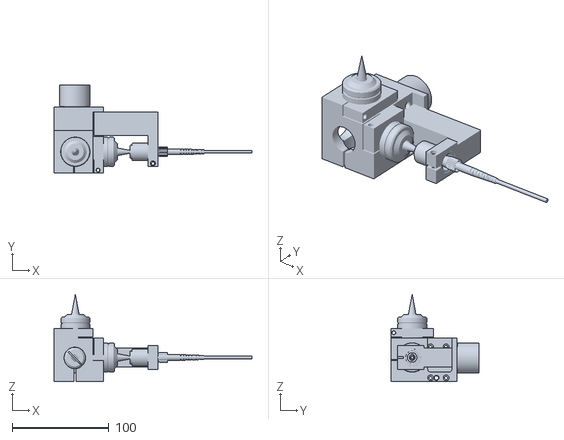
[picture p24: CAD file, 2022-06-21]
CAD_models/Light-Sheet_Unit_Assembly_v6.stl
204.2 x 91.0 x 90.2

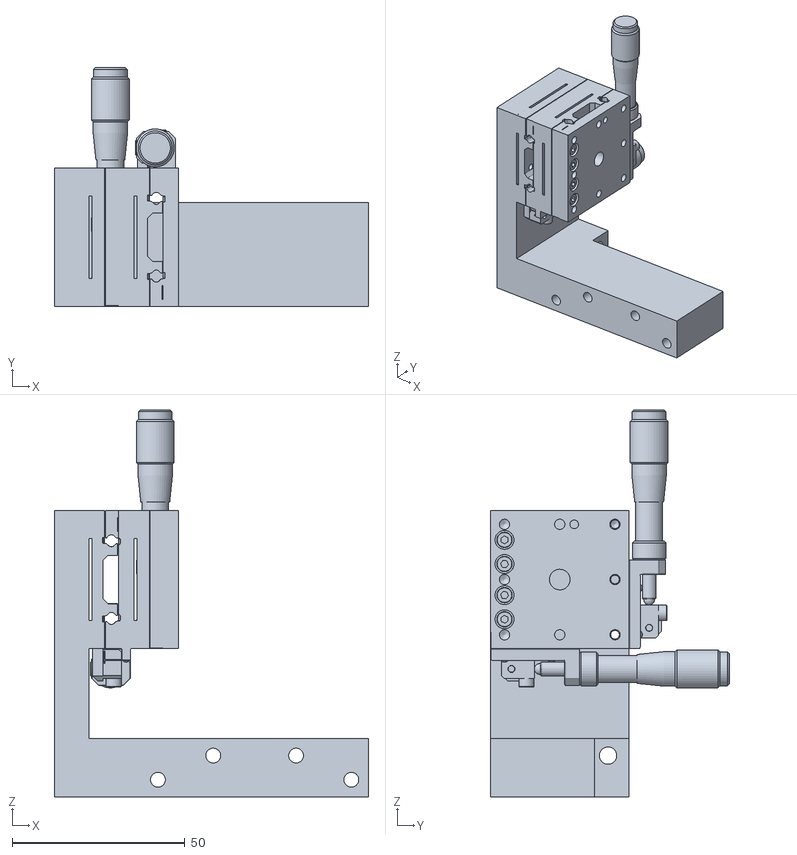
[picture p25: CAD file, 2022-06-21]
CAD_models/Light-Sheet_Holder_Assembly_v3.stl
91.0 x 69.1 x 112.1

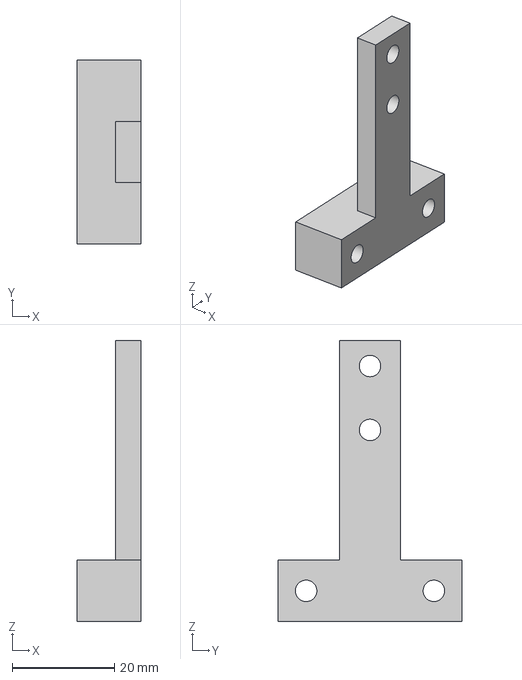
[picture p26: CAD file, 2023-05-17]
CAD_models/TBracket.step
12.5 x 36.0 x 55.0 mm

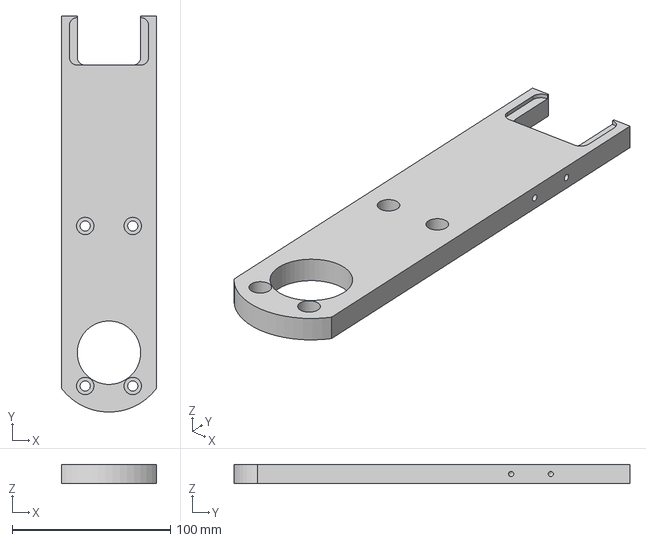
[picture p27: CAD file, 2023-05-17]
CAD_models/SampleChamberHolder.step
60.0 x 249.9 x 12.0 mm

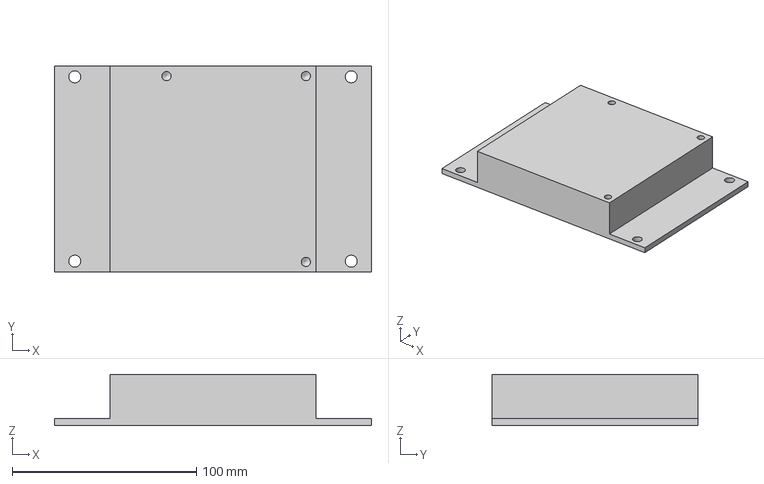
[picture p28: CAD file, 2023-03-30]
CAD_models/NanoMax_Pedestal.step
172.0 x 112.0 x 27.8 mm

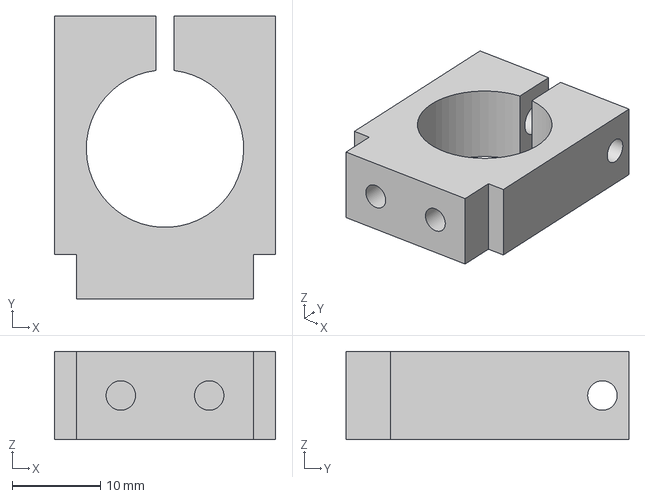
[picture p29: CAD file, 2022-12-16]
CAD_models/FiberHolder.step
25.0 x 32.0 x 10.0 mm

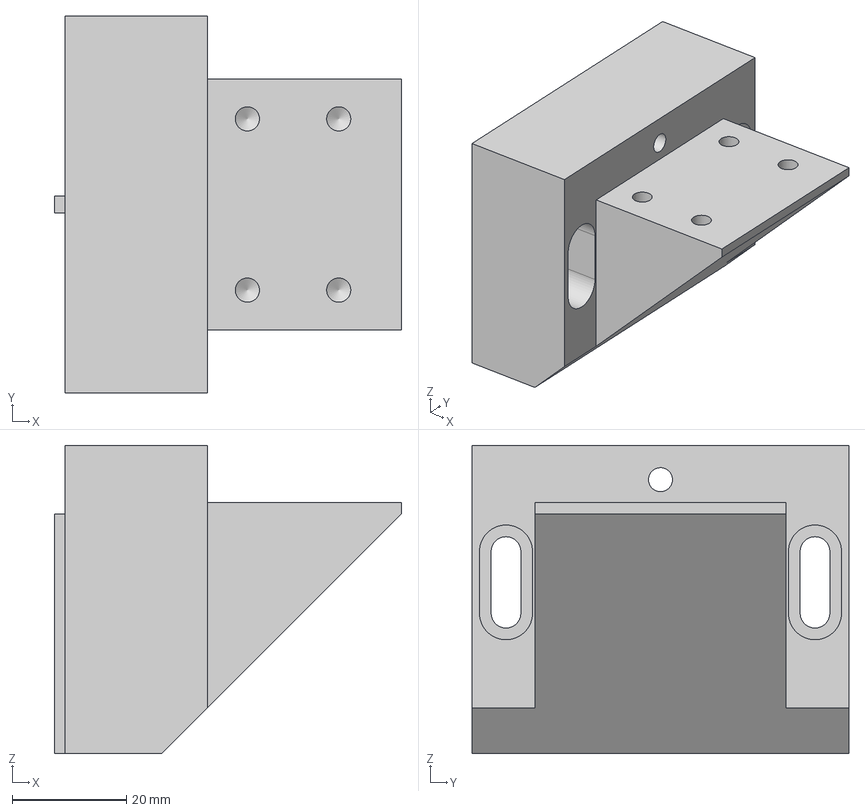
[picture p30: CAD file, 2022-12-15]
CAD_models/CustomBracket.step
60.8 x 66.0 x 54.0 mm

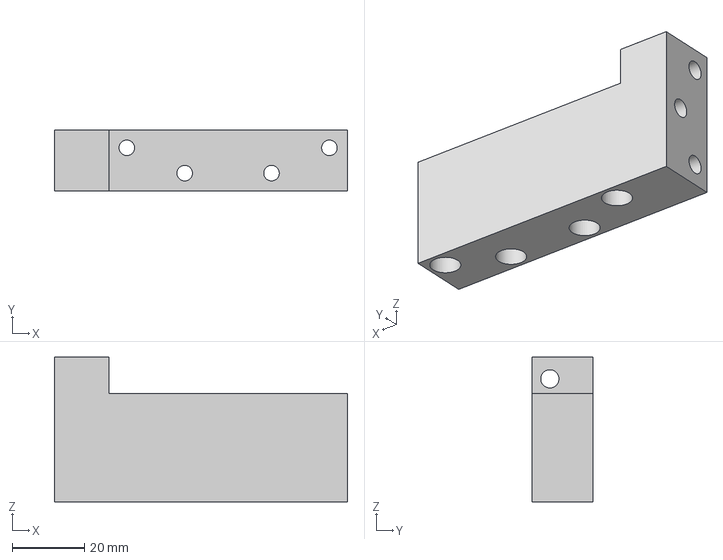
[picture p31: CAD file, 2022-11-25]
CAD_models/AdaptorPlate1.step
81.0 x 17.0 x 40.0 mm

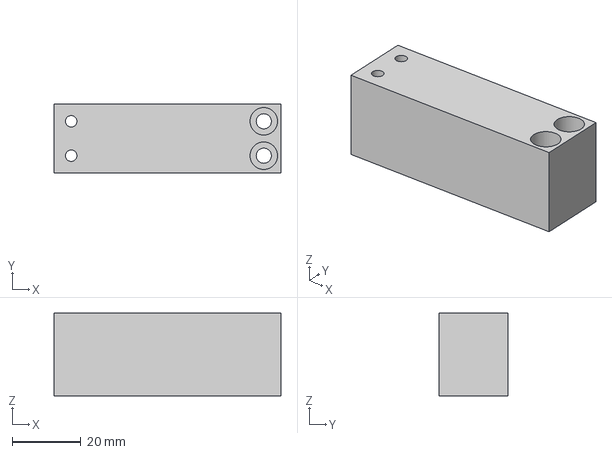
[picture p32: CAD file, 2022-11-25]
CAD_models/PiezoDummy.step
66.0 x 20.0 x 24.0 mm

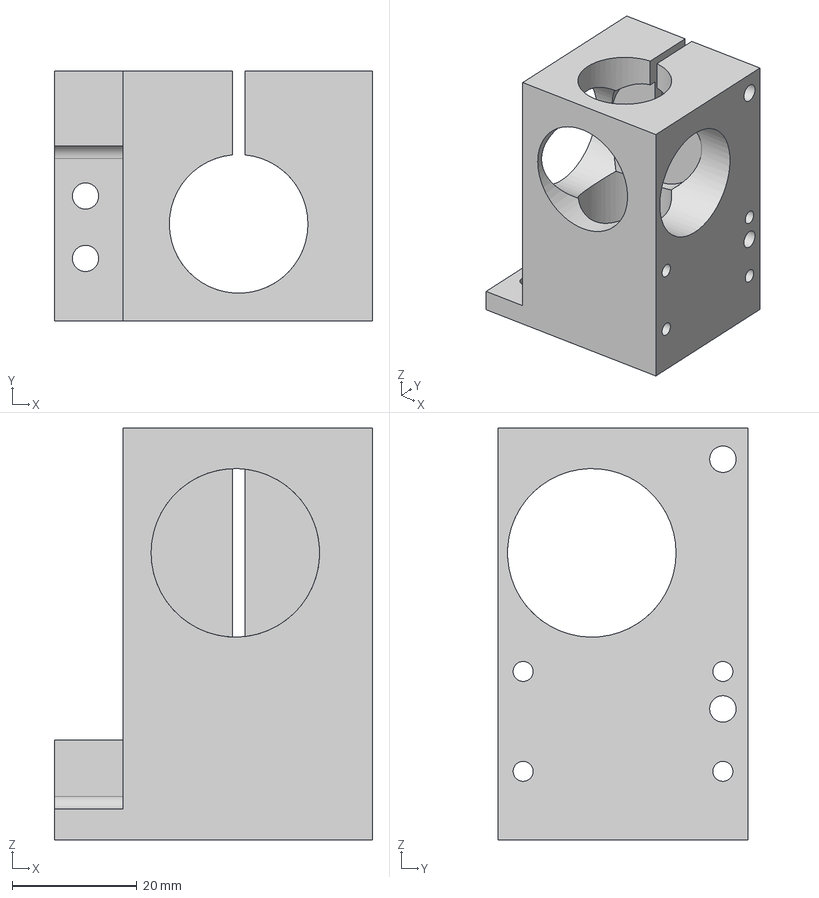
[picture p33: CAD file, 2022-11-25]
CAD_models/Cube.step
51.0 x 40.0 x 66.0 mm

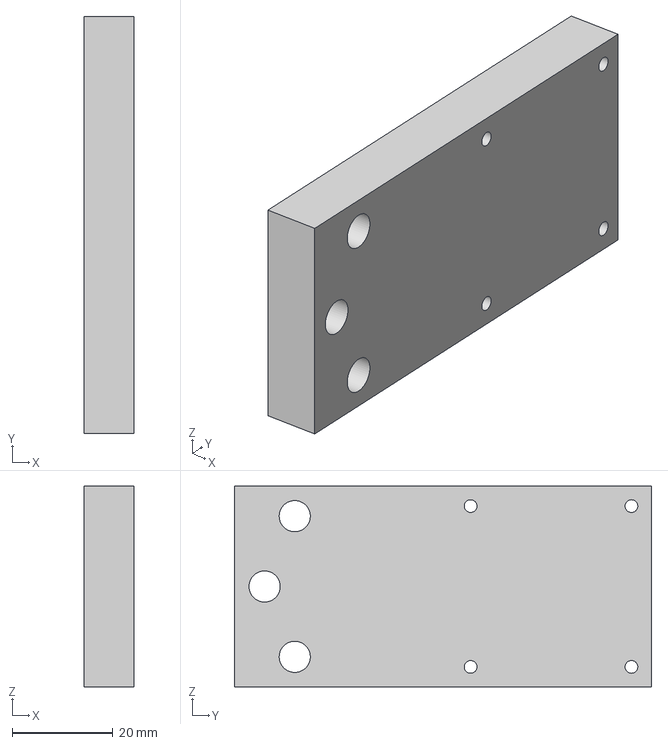
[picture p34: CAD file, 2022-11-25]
CAD_models/AdaptorPlate2.step
10.0 x 83.0 x 40.0 mm

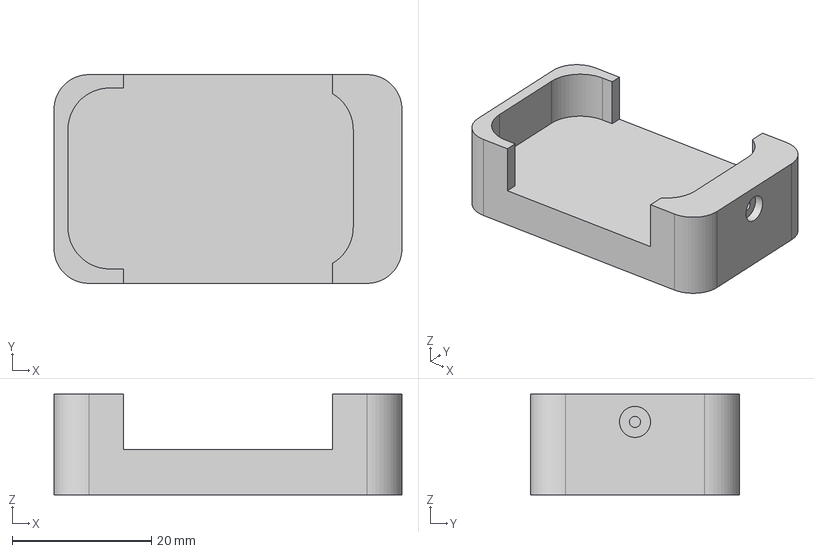
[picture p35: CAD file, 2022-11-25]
CAD_models/SampleChamber.step
50.0 x 30.0 x 14.5 mm

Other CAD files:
CAD_models/AdaptorPlate1.stl
CAD_models/AdaptorPlate2.stl
CAD_models/Cube.stl
CAD_models/CustomBracket.stl
CAD_models/FiberHolder.stl
CAD_models/NanoMax_Pedestal.stl
CAD_models/PiezoDummy.stl
CAD_models/SampleChamber.stl
CAD_models/SampleChamberHolder.stl
CAD_models/TBracket.stl

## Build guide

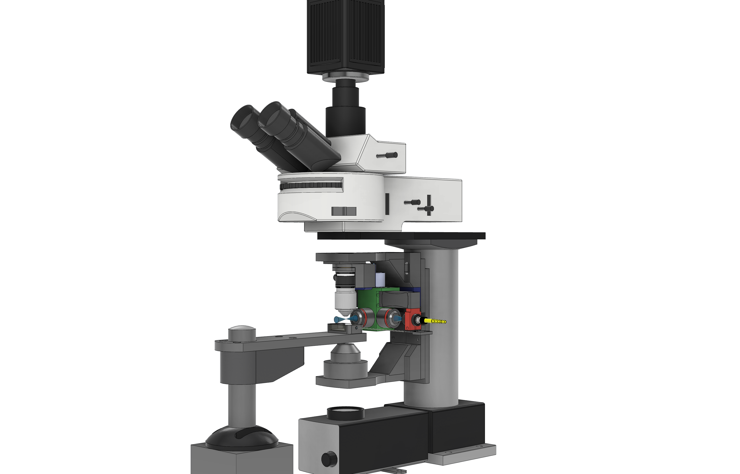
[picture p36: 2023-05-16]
Figures/Braintegration Github Couleurs v1_FullSetup_Front-Right.png

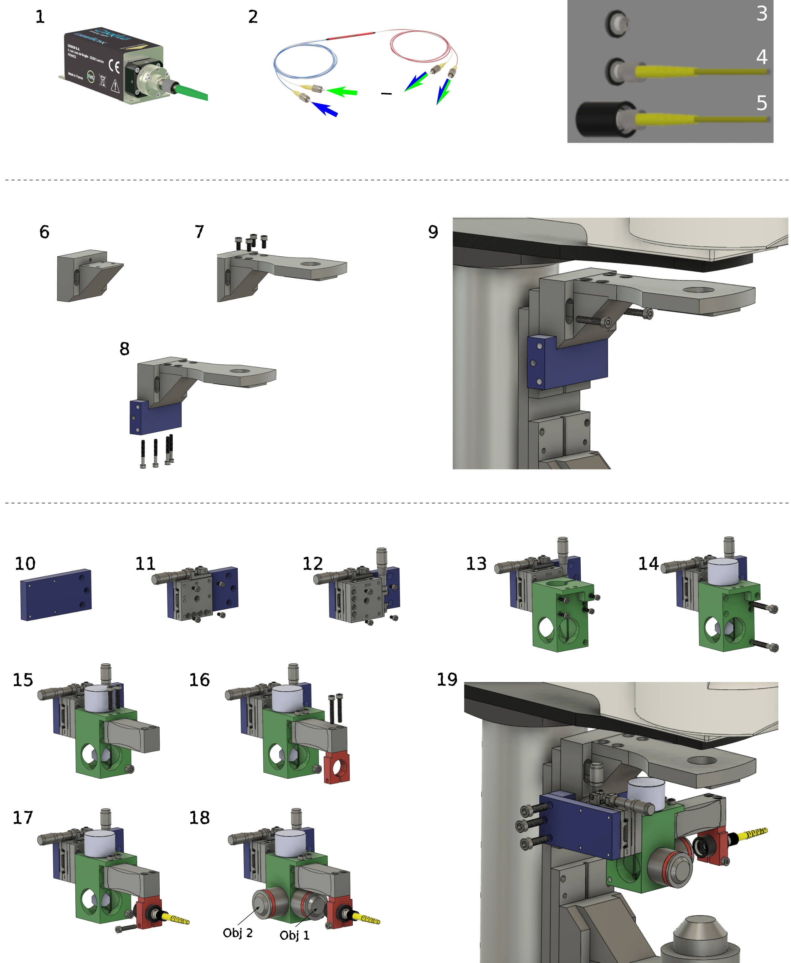
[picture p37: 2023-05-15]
Figures/Assembly_StepByStep.png

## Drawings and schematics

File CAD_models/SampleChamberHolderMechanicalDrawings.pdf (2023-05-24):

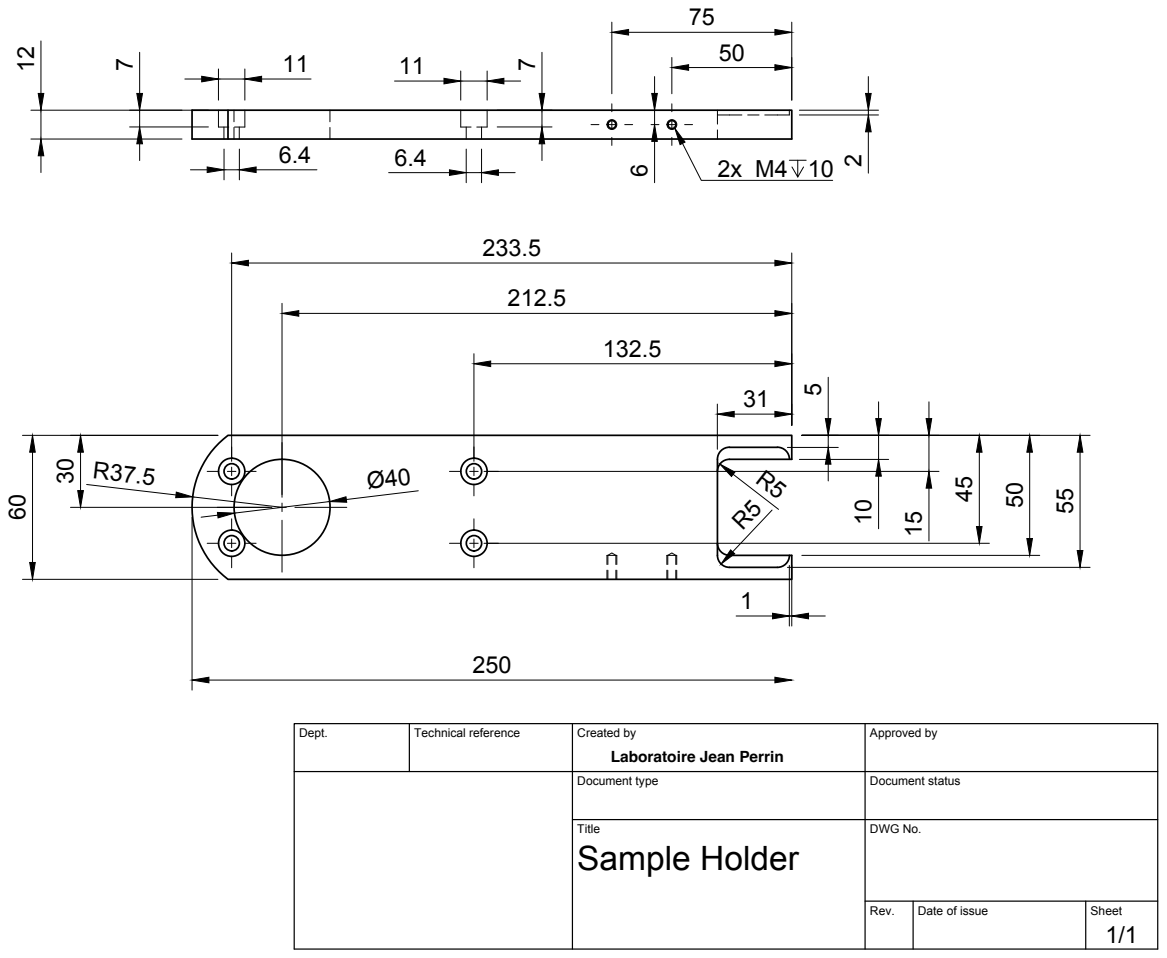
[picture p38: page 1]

Dept. | Technical reference | Created by Thomas Panier 15/12/2022 | Approved by

Document type | Document status

Title Sample Holder | DWG No.

Rev. | Date of issue | Sheet 1/1

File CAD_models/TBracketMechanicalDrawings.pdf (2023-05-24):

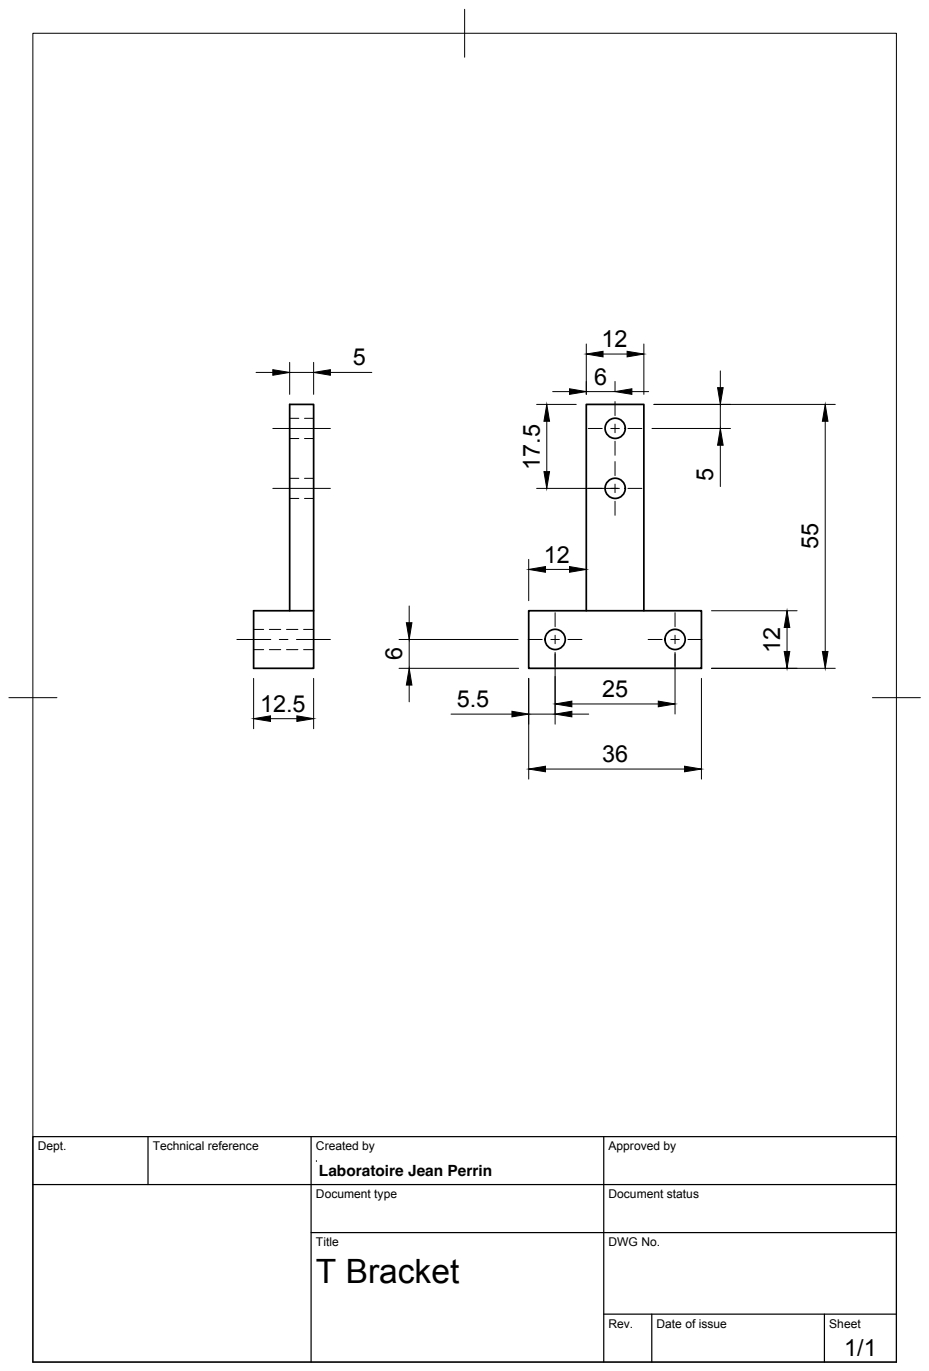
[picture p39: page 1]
Thomas Panier

Dept. | Technical reference | Created by 17/05/2023 | Approved by

Document type | Document status

Title T Bracket | DWG No.

Rev. | Date of issue | Sheet 1/1

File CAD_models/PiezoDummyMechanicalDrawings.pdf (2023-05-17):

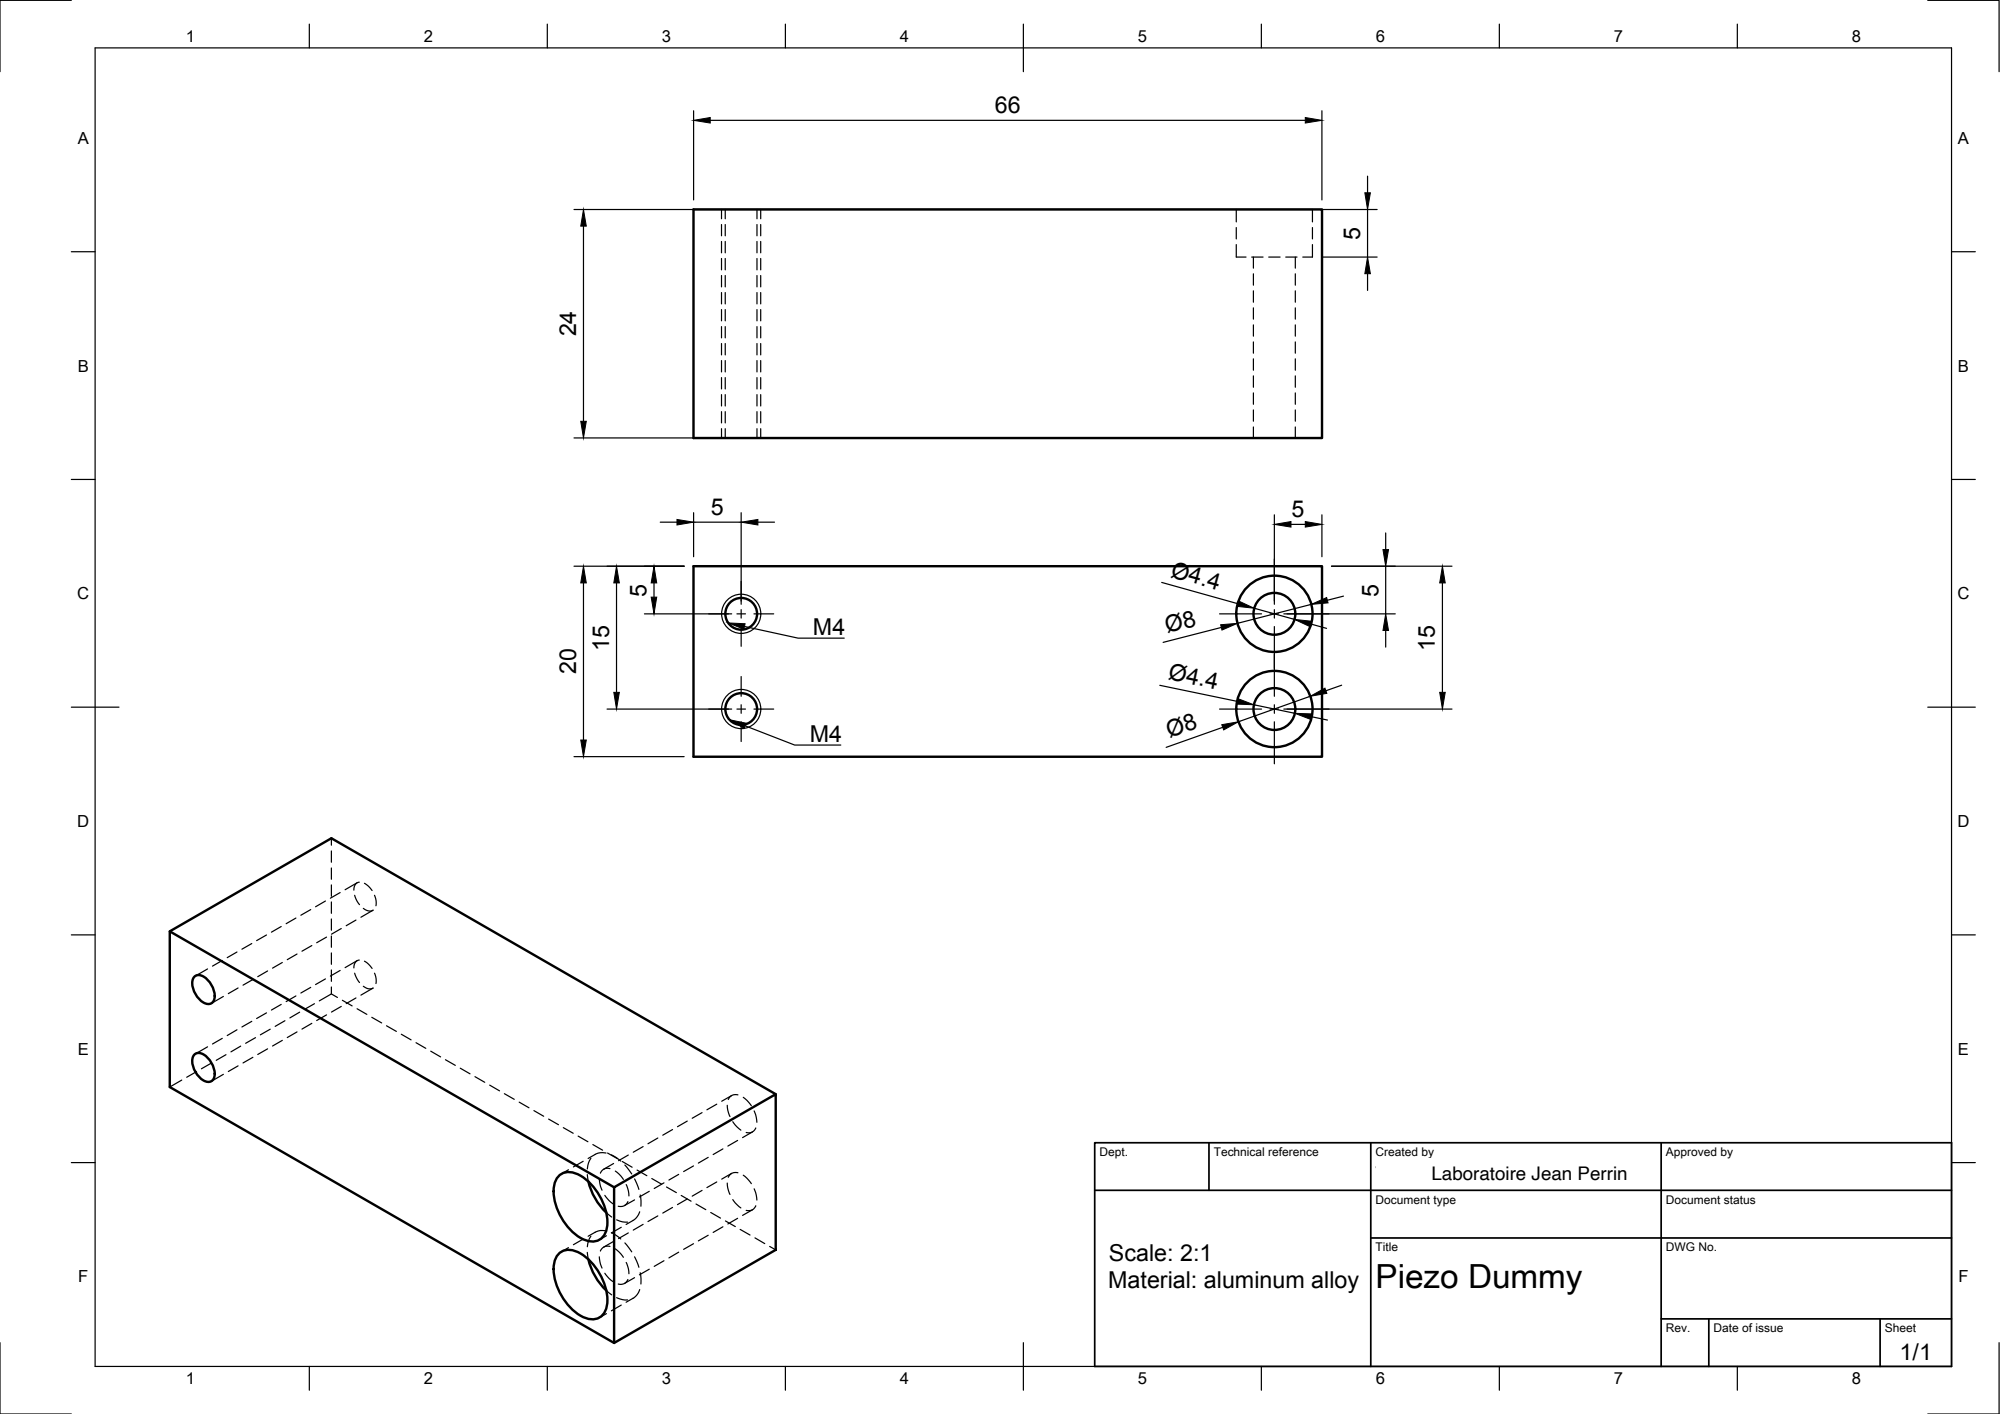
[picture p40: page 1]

Dept. | Technical reference | Created by Thomas Panier 29/09/2017 | Approved by

Scale: 2:1 Material: aluminum alloy | | Document type | Document status

Title Piezo Dummy | DWG No.

Rev. | Date of issue | Sheet 1/1

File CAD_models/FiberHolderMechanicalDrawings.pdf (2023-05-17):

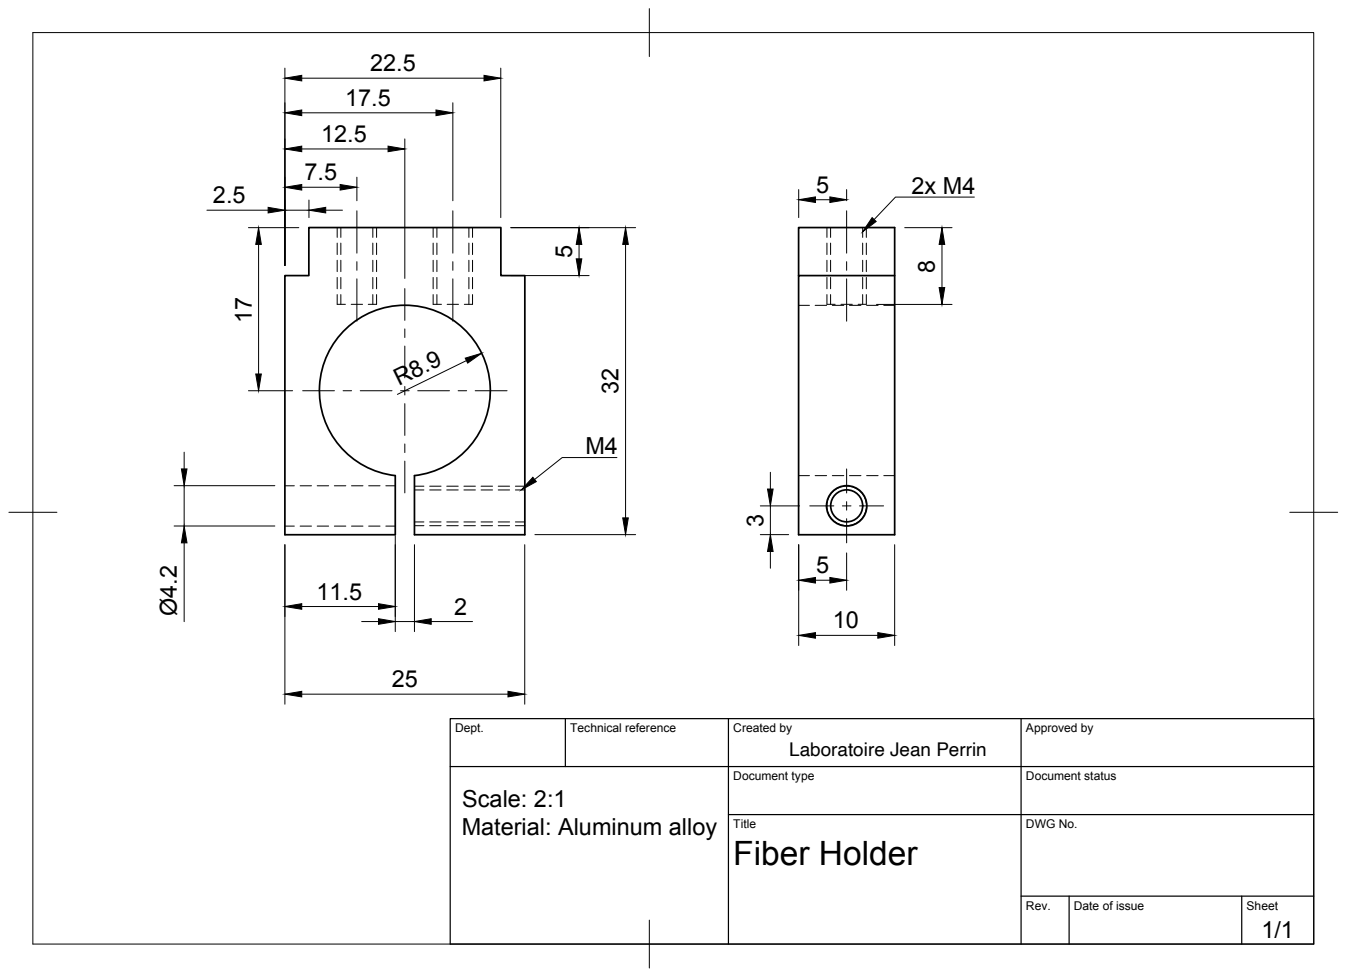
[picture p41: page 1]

Dept. | Technical reference | Created by Thomas Panier 25/11/2022 | Approved by

Scale: 2:1 Material: Aluminum alloy | | Document type | Document status

Title Fiber Holder | DWG No.

Rev. | Date of issue | Sheet 1/1

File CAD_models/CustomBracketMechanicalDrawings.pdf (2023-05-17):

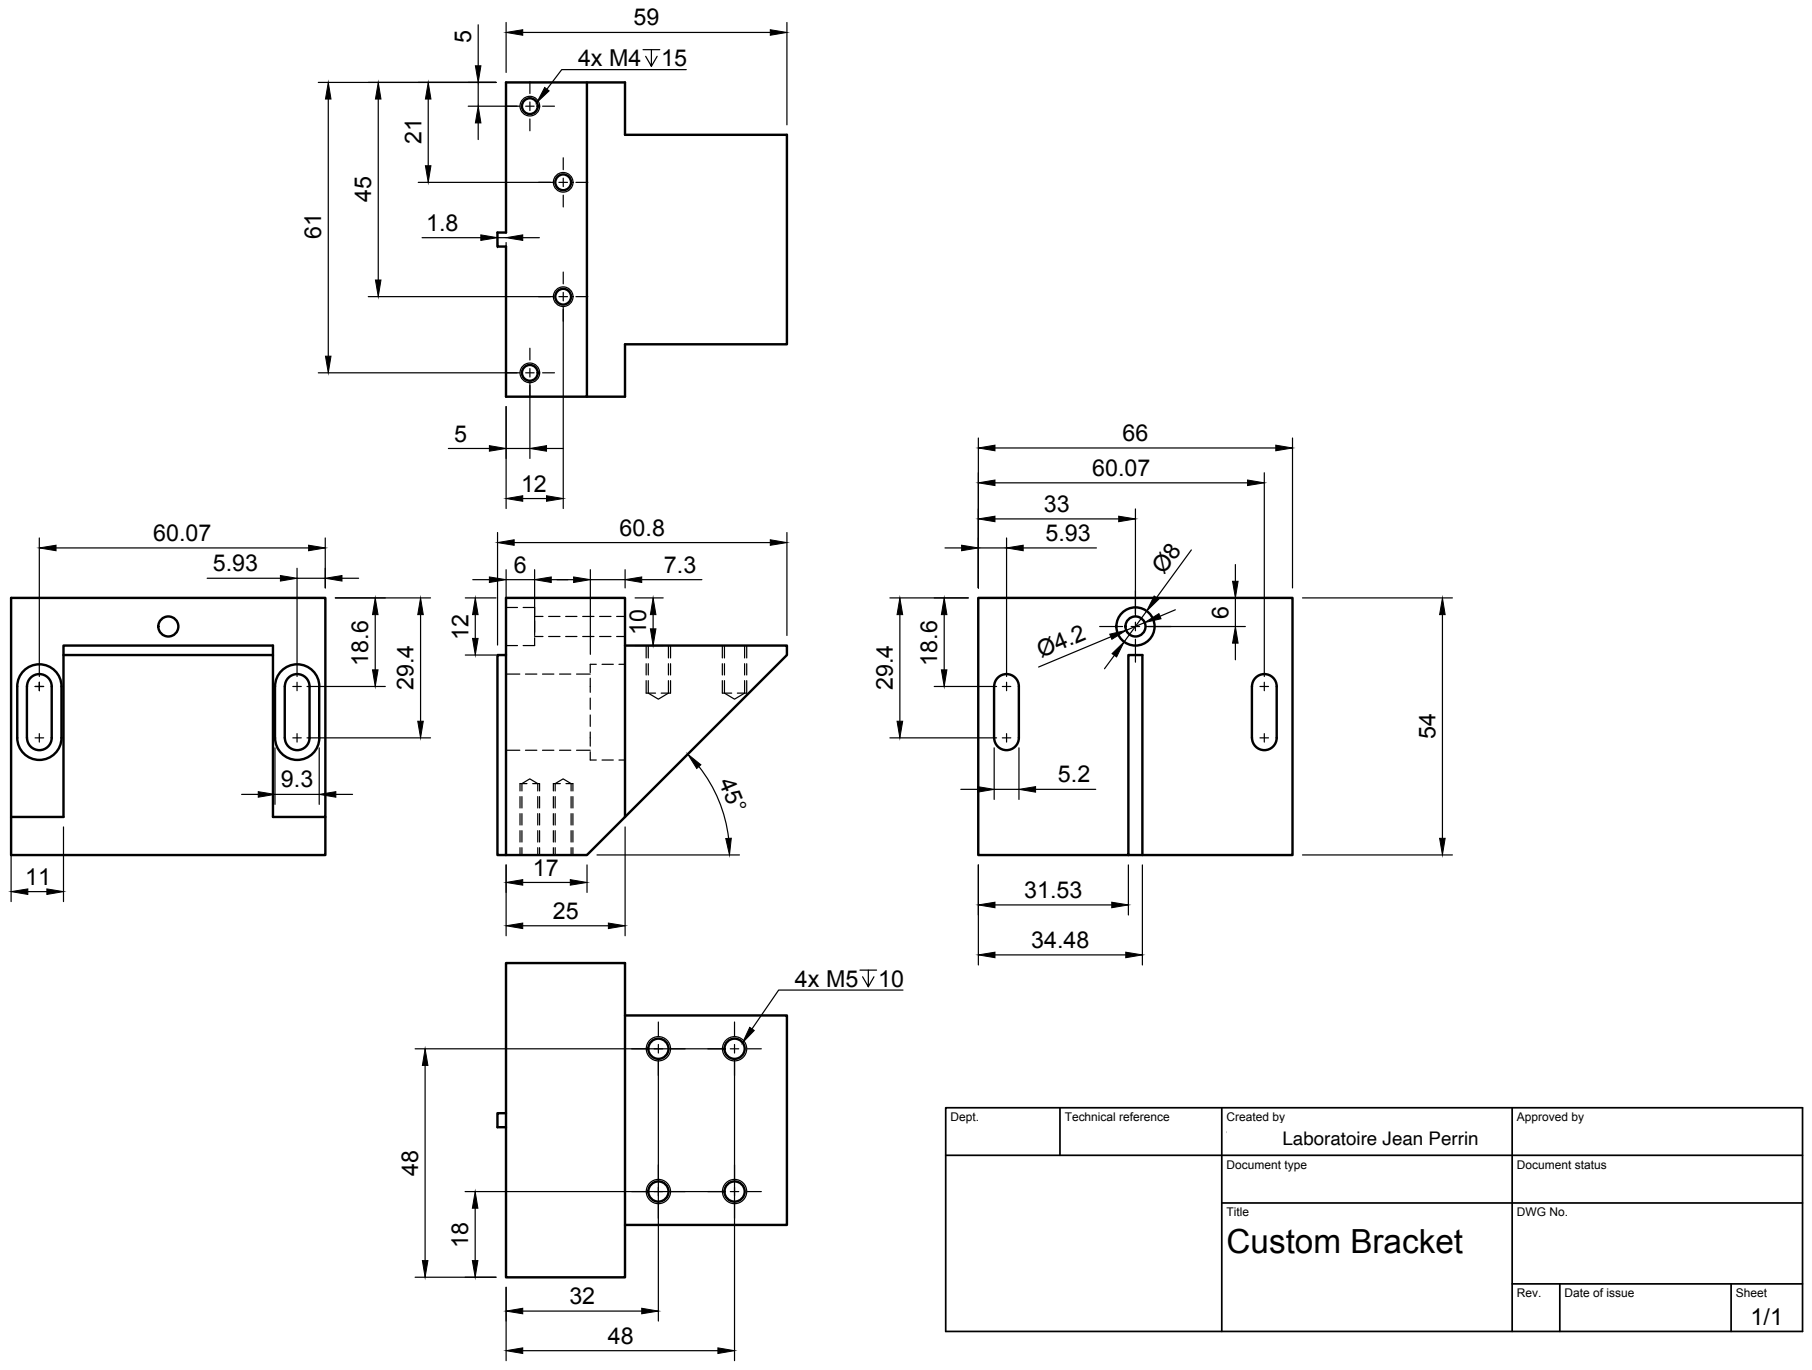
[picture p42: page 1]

Dept. | Technical reference | Created by Thomas Panier 08/11/2022 | Approved by

Document type | Document status

Title Custom Bracket | DWG No.

Rev. | Date of issue | Sheet 1/1

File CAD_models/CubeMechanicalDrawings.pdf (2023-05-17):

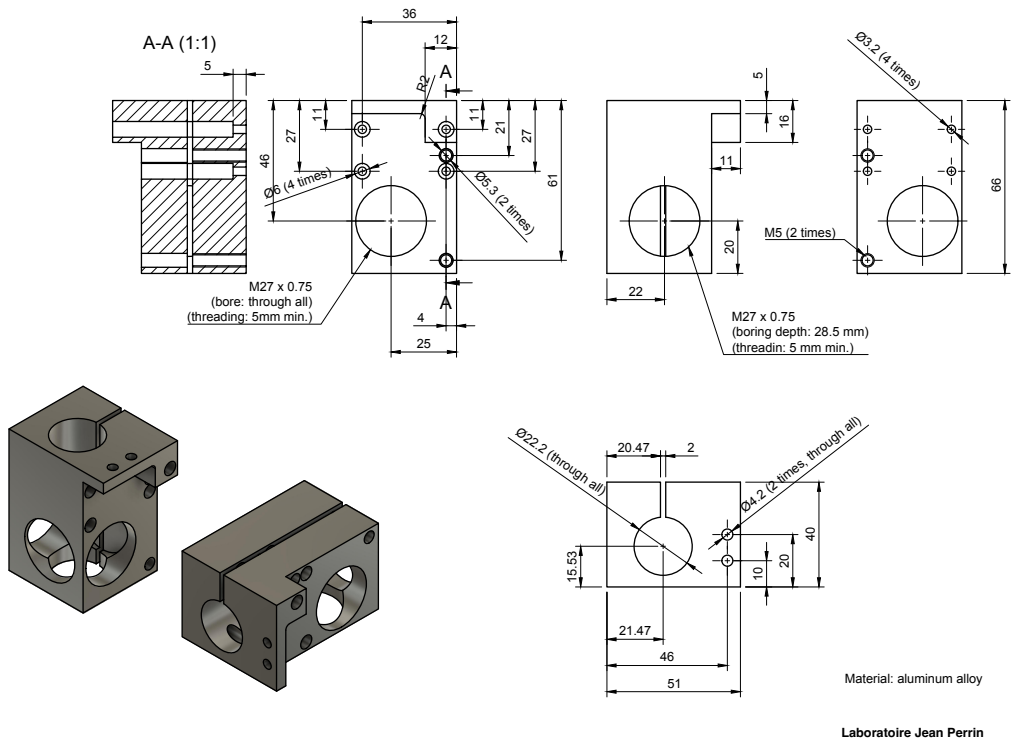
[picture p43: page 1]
Ø22.2 (through all); 4 46 Ø6 (4 times) Ø5.3 (2 times); M5 (2 times); Ø3.2 (4 times); (threading: 5mm min.)

(bore: through all)

(boring depth: 28.5 mm)
(threadin: 5 mm min.)

Ø4.2 (2 times, through all)

Material: aluminum alloy

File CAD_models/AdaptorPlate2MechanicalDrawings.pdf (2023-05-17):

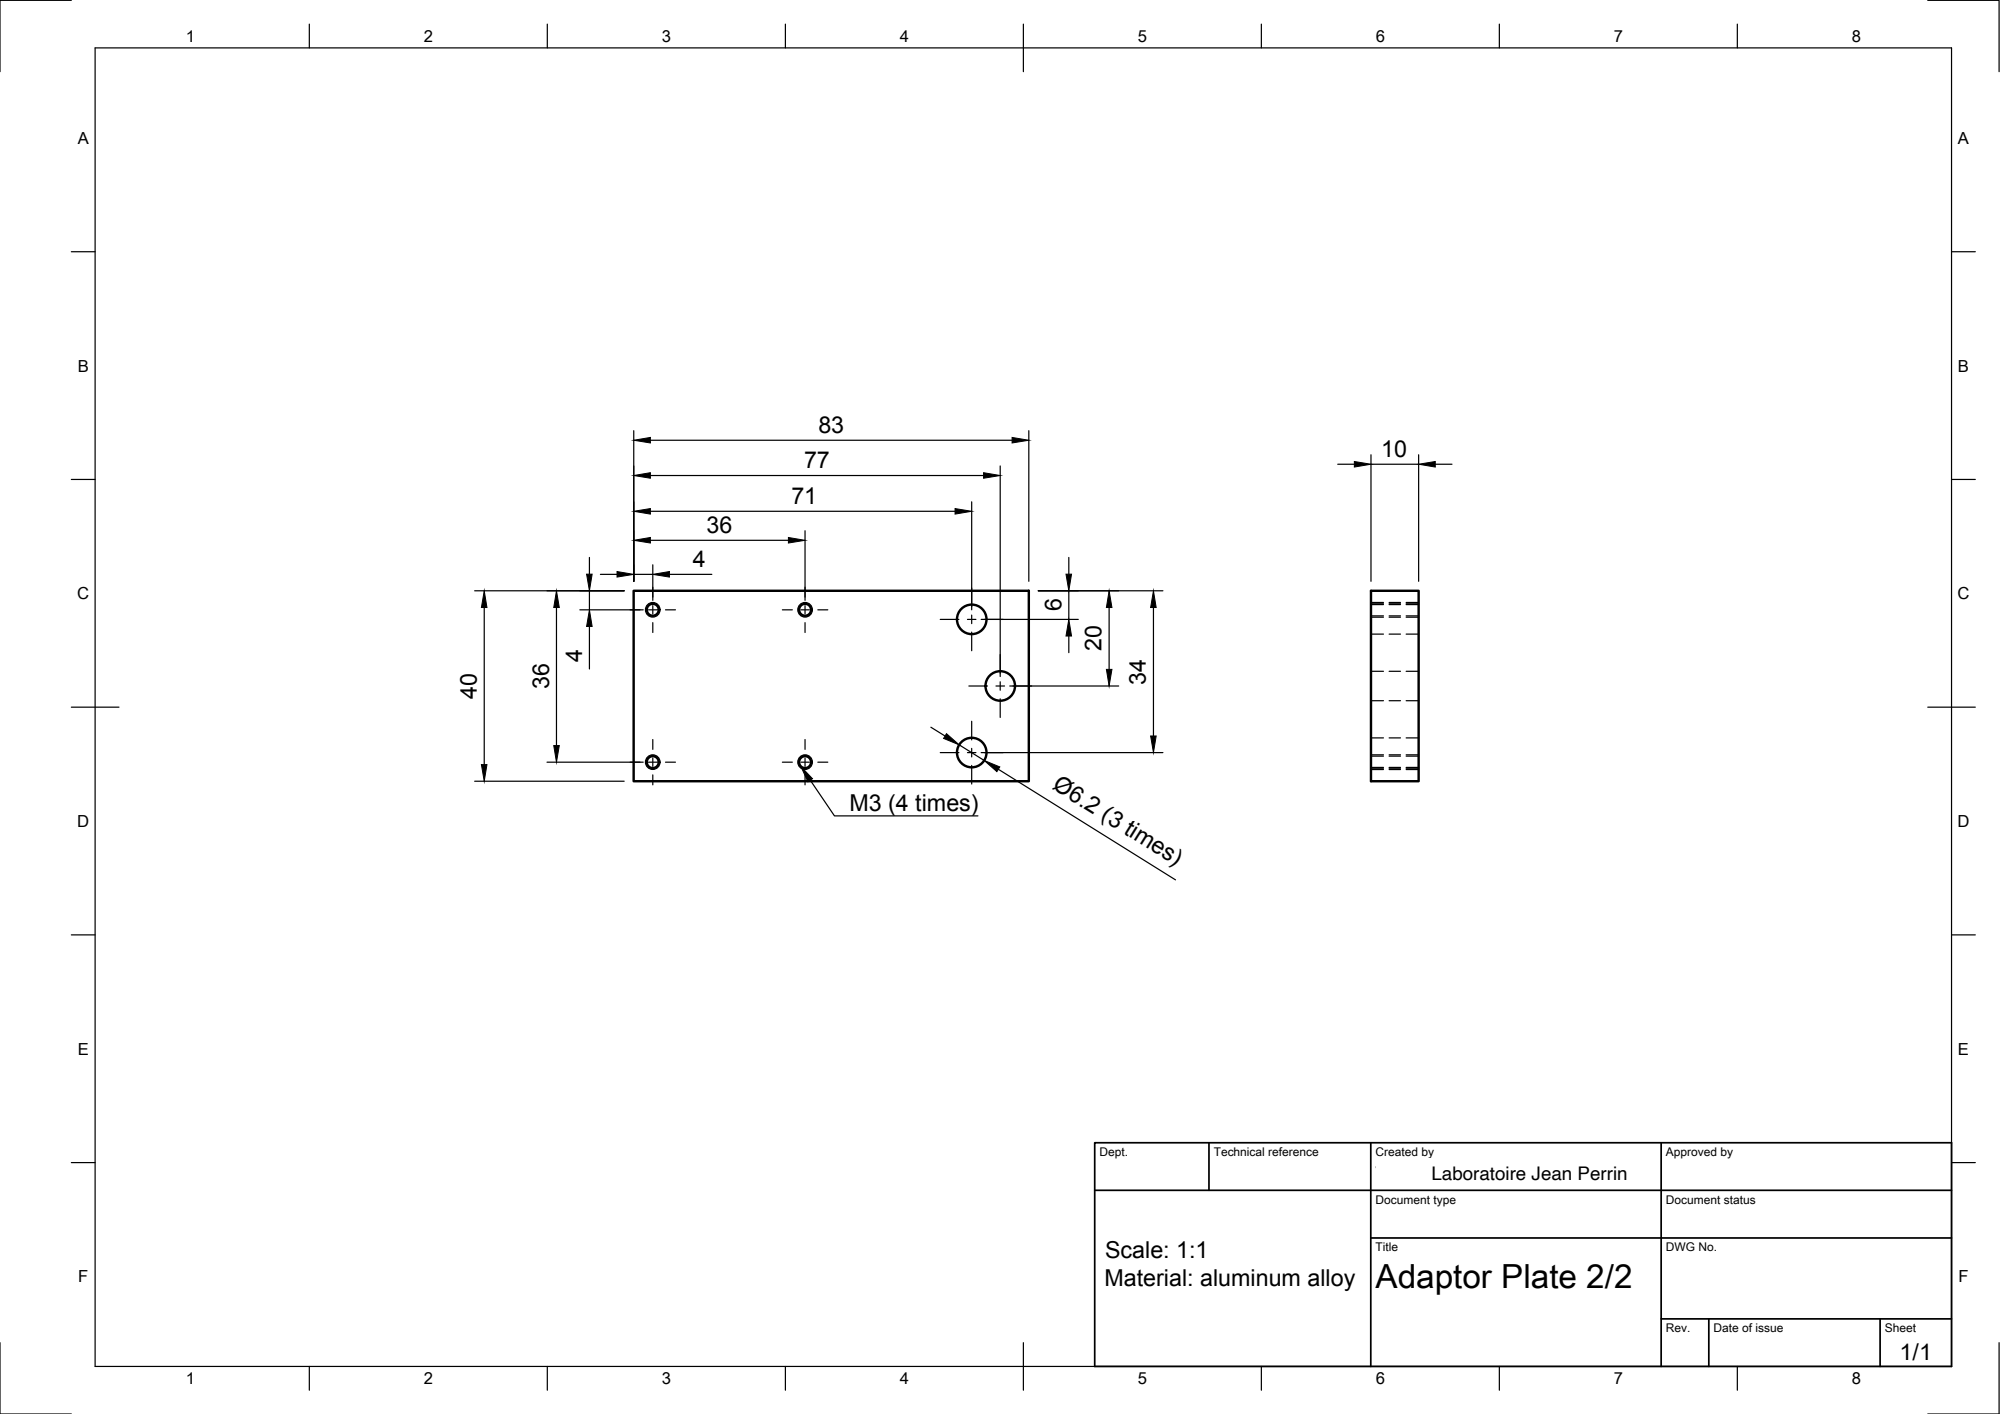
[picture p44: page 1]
M3 (4 times); Ø6.2 (3 times)

Dept. | Technical reference | Created by Thomas Panier 29/09/2017 | Approved by

Scale: 1:1 Material: aluminum alloy | | Document type | Document status

Title Adaptor Plate 2/2 | DWG No.

Rev. | Date of issue | Sheet 1/1

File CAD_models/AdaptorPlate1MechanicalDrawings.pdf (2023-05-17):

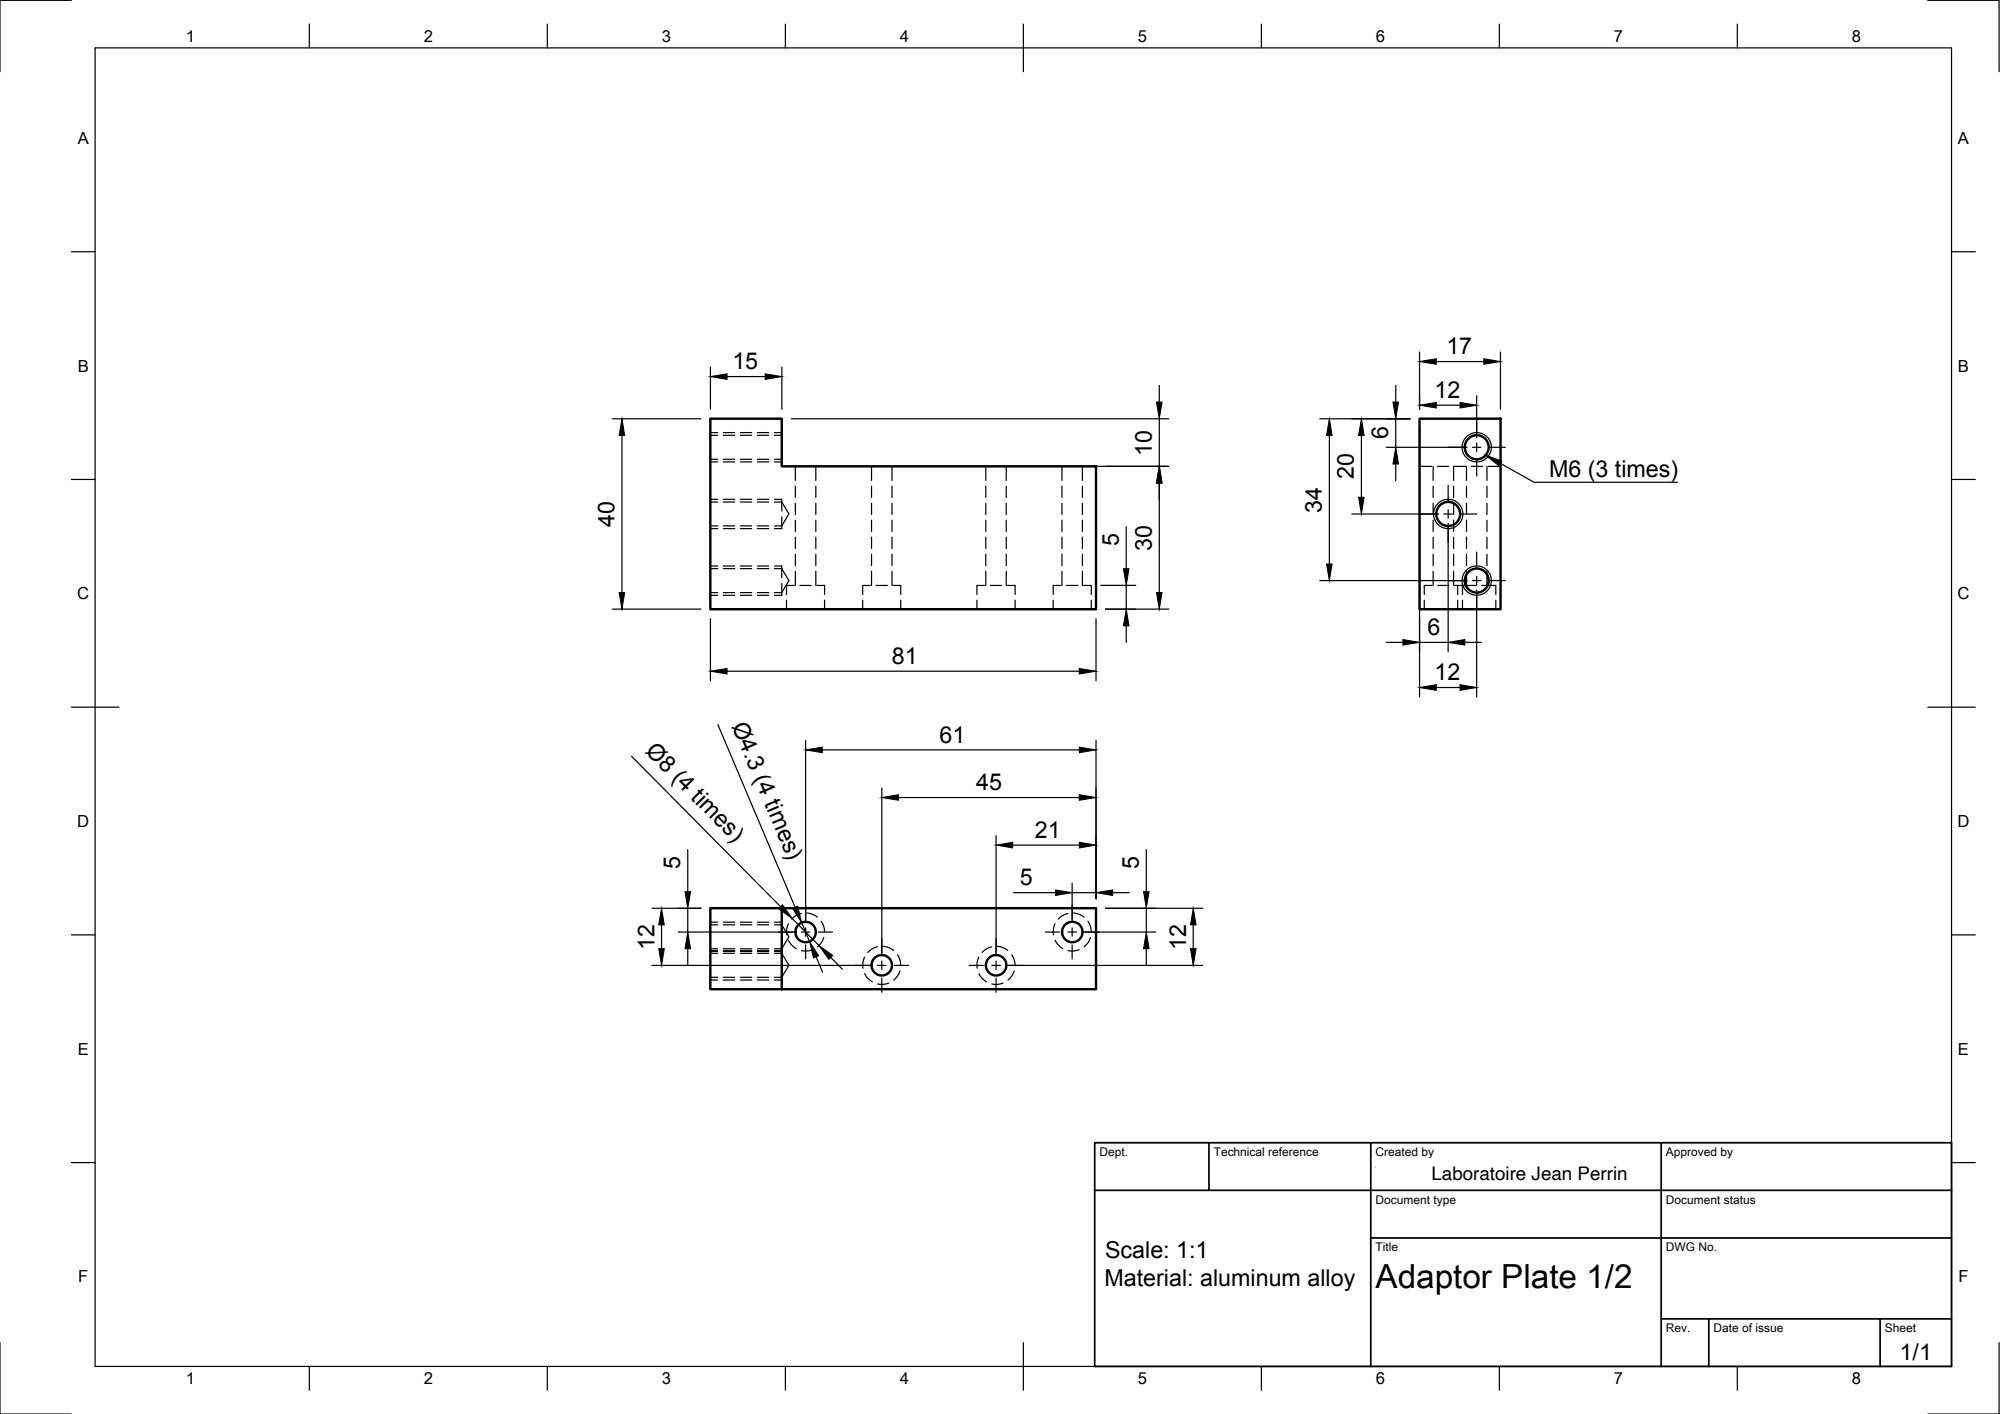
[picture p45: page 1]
Thomas Panier 40; M6 (3 times); Ø4.3 (4 times) Ø8 (4 times)

Dept. | Technical reference | Created by 29/09/2017 | Approved by

Scale: 1:1 Material: aluminum alloy | | Document type | Document status

Title Adaptor Plate 1/2 | DWG No.

Rev. | Date of issue | Sheet 1/1

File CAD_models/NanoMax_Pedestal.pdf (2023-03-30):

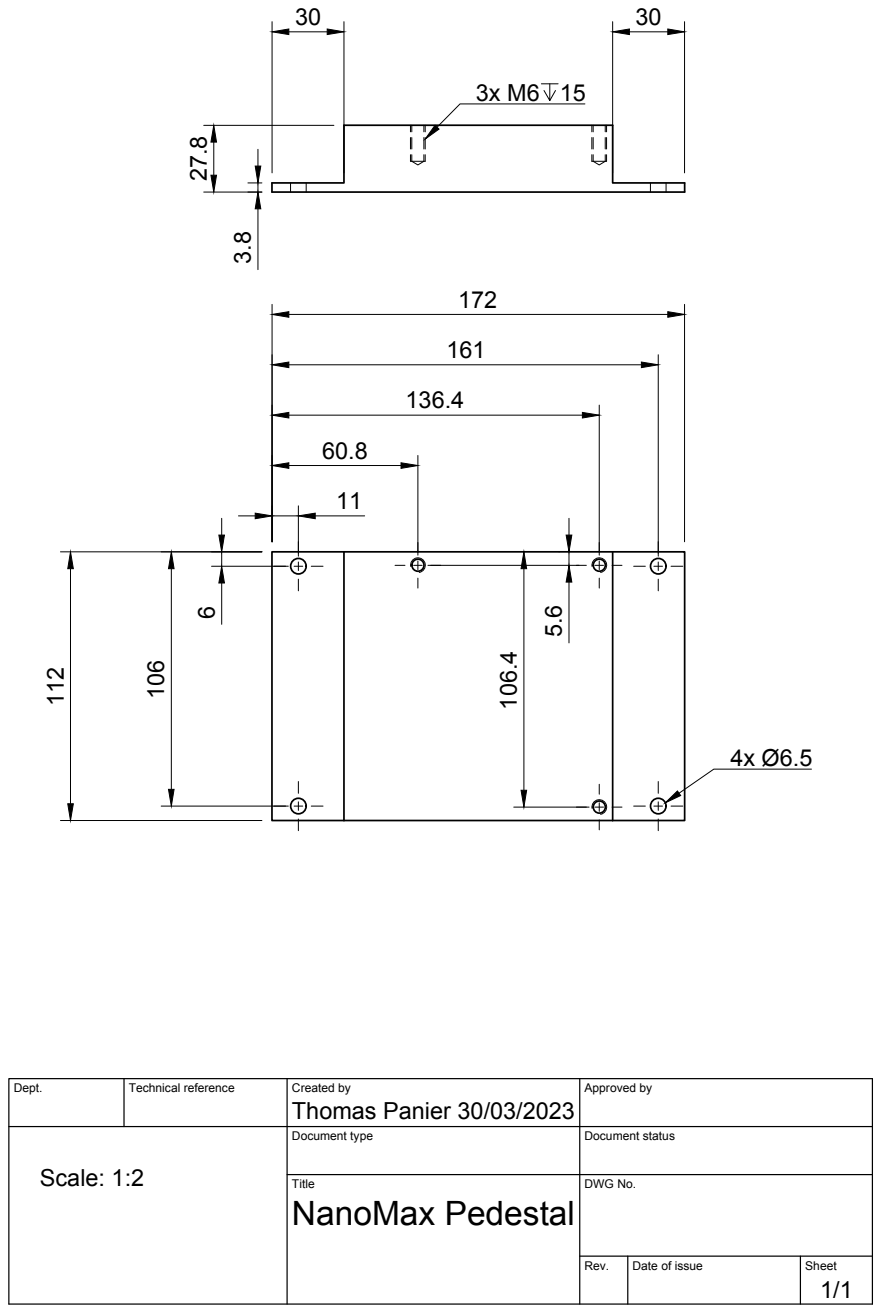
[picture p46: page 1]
Scale: 1:2

Dept. | Technical reference | Created by Thomas Panier 30/03/2023 | Approved by

Document type | Document status

Title NanoMax Pedestal | DWG No.

Rev. | Date of issue | Sheet 1/1

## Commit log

2022-11-25 'Pieces to send for milling' update and cleanup
2022-12-15 Update 1P_Multicolor_System.md
    Custom Bracket links in Pieces to mill
2022-12-15 Add files via upload
    Custom Bracket files
    [CustomBracket.step]
2022-12-15 Sample Holder files
    [SampleHolder.step, SampleHolder.stl]
2022-12-16 Update FiberHolder files
    [FiberHolder.step, FiberHolder.stl]
2022-12-16 FiberHolder update
    [FiberHolder.step, FiberHolder.stl]
2023-05-15 uploaded new assembly figure
2023-05-15 Update 1P_Multicolor_System.md
    added new assembly_step_by_step.png figure
2023-05-24 figure upload
    [SampleChamberHolder.step, SampleChamberHolder.stl]
